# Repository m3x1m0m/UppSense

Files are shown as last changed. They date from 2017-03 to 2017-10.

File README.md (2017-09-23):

UppSense

UppSense17- Open Source sensor for chemical analysis based on fuoresence.
 
## Hardware
Hardware Block Diagram

The hardware consists out of three PCBs so far: An analog PCB, a digital PCB and an active Backplane. Two PCBs are developed with KiCAD. One is developed with Altium.

A transimpedance amplifier is used to convert light into a voltage. With a
second stage this voltage is amplified. Both outputs are available for the ADC. 

On the digital board there is besides an ESP8266, an ADC, a DAC and a temperature
sensor. The DAC is needed to steer the LED driver circuit, that excites the
sample. 
 
## Software
UML Diagram

The software is written in C++ leveraging the
[Sming](https://github.com/SmingHub/Sming) framework. This enables IoT
applications very easily.

In the UML diagram above it is examplarily shown how the software works. Providers
and receivers can be tied together in pairs to enable an easy way to exchange
data. 

[Software Documentation](http://uppsense.eu/swdoc/)

## Web & Contact
Website: www.uppsense.eu | Email: contact@uppsense.eu

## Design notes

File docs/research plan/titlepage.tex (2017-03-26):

%%%%%%%%%%%%%%%%%%%%%%%%%%%%%%%%%%%%%%%%%%%%%%%%%%%%%%%%%%%%%%%%%%%%%%%%%%%%%%%%%%%%%%
%% Author:      Maximilian Stiefel
%% Date:        06.03.2017
%% University:  Uppsala Universitet
%% Department:  Institutionen för informationsteknologi 
%% Course:      Microcontroller Programming
%% Project:     Swakeup
%%%%%%%%%%%%%%%%%%%%%%%%%%%%%%%%%%%%%%%%%%%%%%%%%%%%%%%%%%%%%%%%%%%%%%%%%%%%%%%%%%%%%%

\begin{titlepage}
% temporary margins only for titlepage
\newgeometry{lmargin={2cm},rmargin={2cm},tmargin={1cm},bmargin={2cm}}

%---------------------- Figures --------------------------------------------------

\begin{figure}
	\raggedright
	%\raggedleft
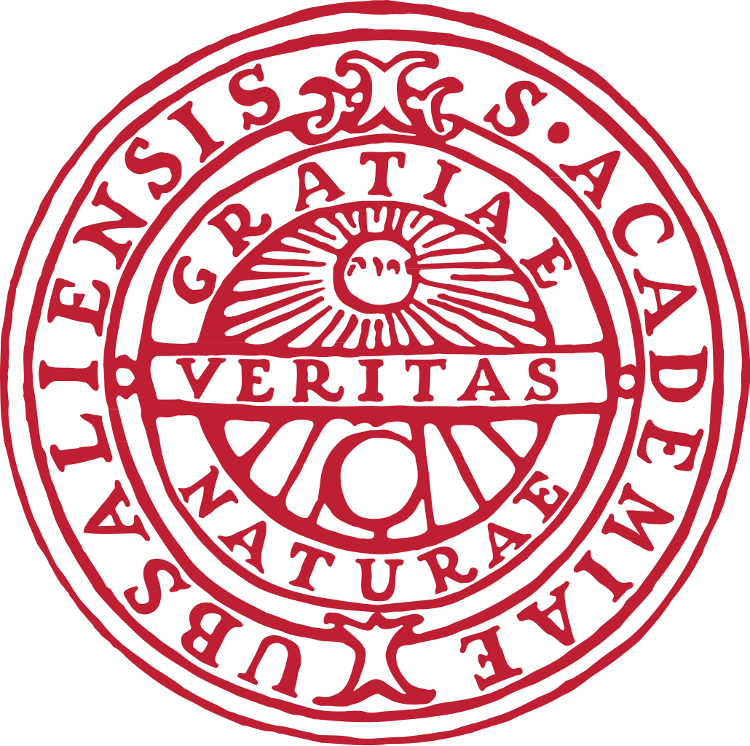
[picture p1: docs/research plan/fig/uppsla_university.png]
	
\end{figure}

%---------------------- Text -----------------------------------------------------

\begin{center}
	\vspace*{0pt}
	\begin{Huge}
		\textbf{\mytitle}\\
	\end{Huge}
	\vspace*{4em}
	\begin{LARGE}
		\textbf{\MakeUppercase{\mytypeofwork}}\\
	\end{LARGE}	
	\vspace*{2em}
	within the lecture of\\
	\mycourse\\
	\vspace*{2em}
	at \myuniversity\\
	in the Departement of \mydepartement\\
	\vspace*{2em}
	\myauthora{}, \myauthorb{} and \myauthorc\\
	\vspace*{2em}
	Deadline: \myduedate\\
	\vspace*{3em}
	\vfill
%---------------------- Table ----------------------------------------------------
	
	\setlength{\tabcolsep}{24pt}	% change space between rows
	\begin{tabular}{ll}
		Processing Period:&  \myperiod\\
		Supervisor:&\mytutor\\
		Document Revision:& \myrev\\
		Last Change:& \today\\
	\end{tabular}
	\setlength{\tabcolsep}{6pt}		% back to default
	\restoregeometry
\end{center}
\end{titlepage}
\clearpage

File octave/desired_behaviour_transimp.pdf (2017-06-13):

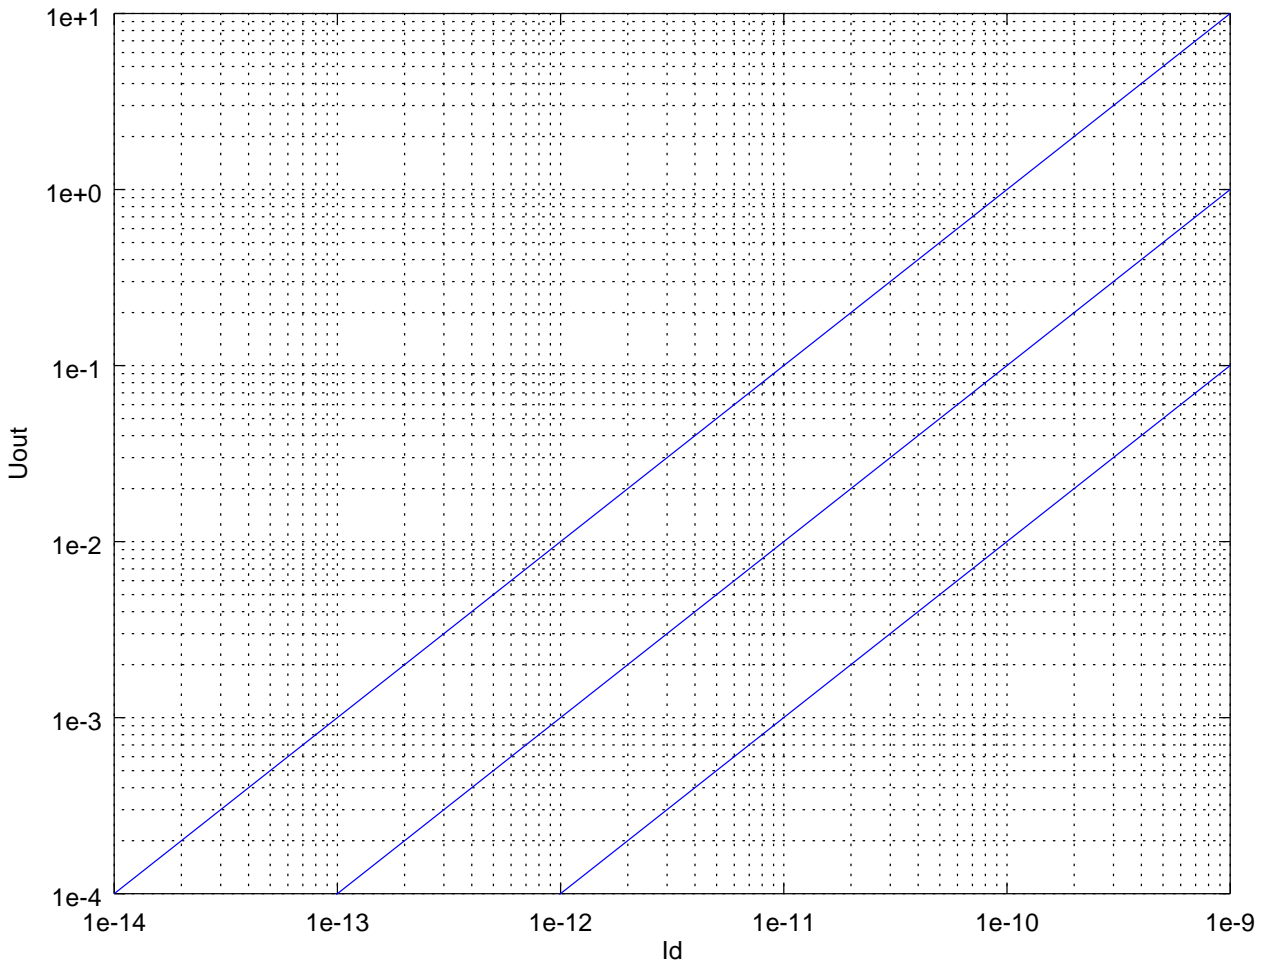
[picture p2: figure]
Uout

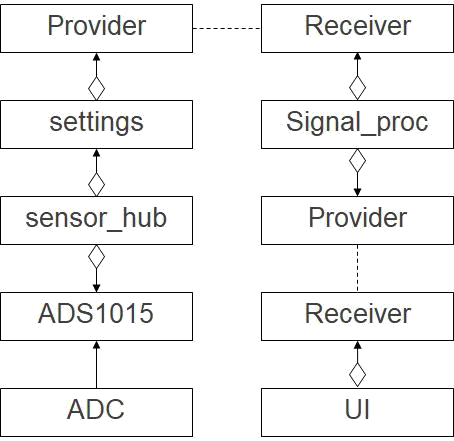
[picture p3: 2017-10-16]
docs/presentations/fig/sw_architecture.png

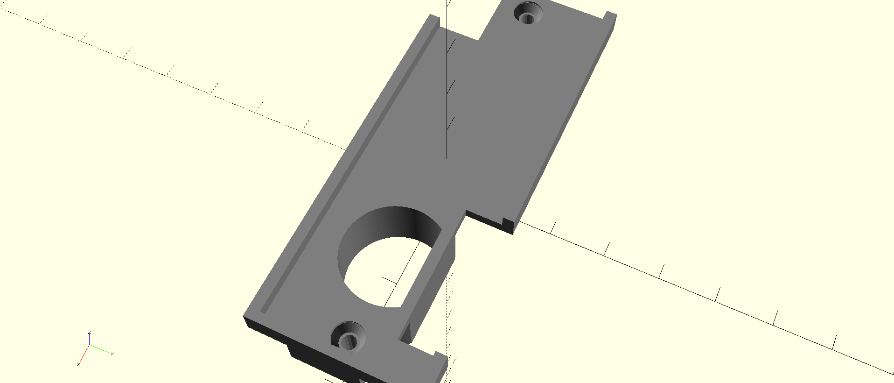
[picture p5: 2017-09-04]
cad/mechanics_rev6/pcb/screen_shot_2.png

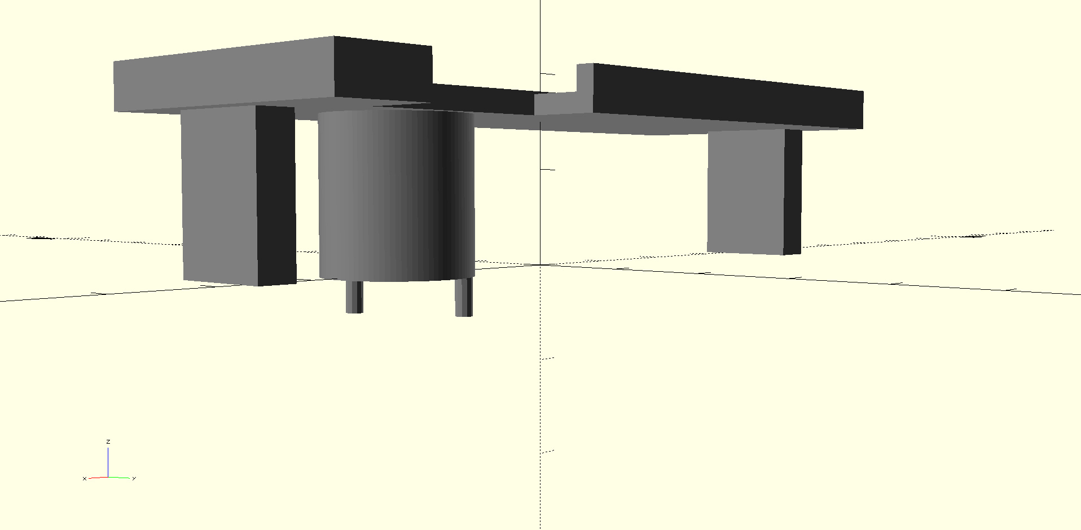
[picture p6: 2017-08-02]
cad/mechanics_rev6/pcb/screenshot_2.png

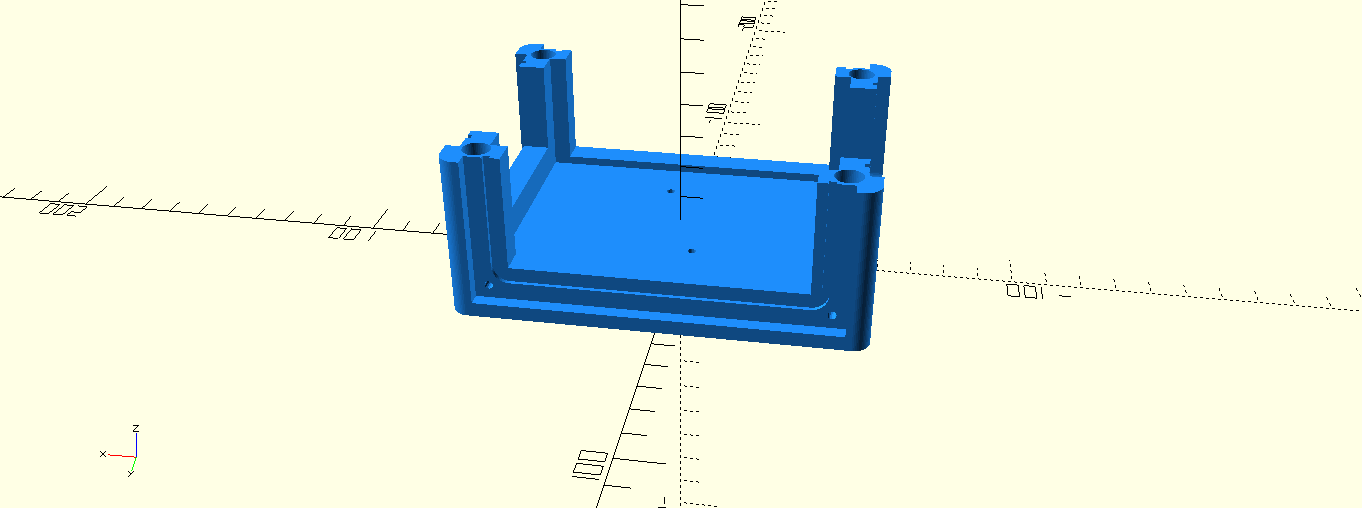
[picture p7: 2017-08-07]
cad/mechanics_rev6/housing/screenshot_female.png

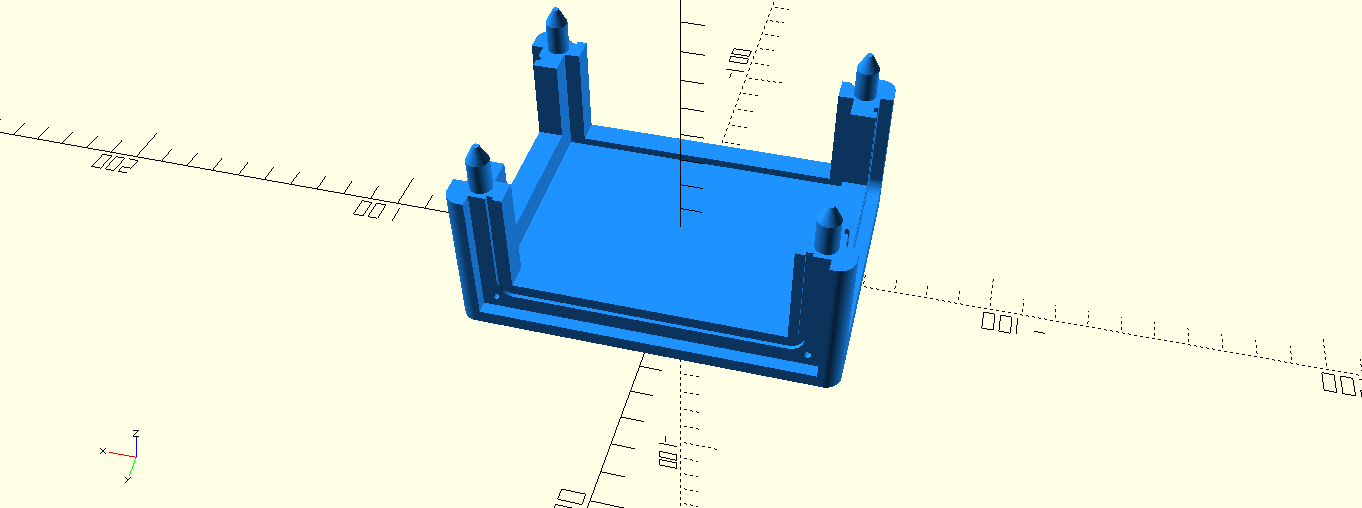
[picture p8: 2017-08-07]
cad/mechanics_rev6/housing/screenshot_male.png

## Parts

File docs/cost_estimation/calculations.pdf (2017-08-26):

Sheet1

Total | €40.00
Margin | €11.03
Ananlog Board | Price | Number
Passives | €0.05 | 34 €1.70
BPW34FA | €0.40 | 1 €0.40
BPW34 | €0.40 | 1 €0.40
UV LED | €0.10 | 1 €0.10
Connector Samtec 02x03 | €1.00 | 1 €1.00
Connector Samtec 02x07 | €1.00 | 1 €1.00
Transistor MMBT3904 | €0.05 | 1 €0.05
Opamp LTC6268 | €3.20 | 1 €3.20
Opamp ADA4522 | €1.20 | 1 €1.20
Opamp LM358 | €0.07 | 1 €0.07
Charge Pump ICL7660S | €0.09 | 2 €0.18
PCB | €0.50 | 1 €0.50
| | €9.80
Digital Board | Price | Number
Passives | €0.05 | 26 €1.30
ADS1115 | €3.00 | 1 €3.00
DAC101C085 | €0.70 | 1 €0.70
MCP9808 | €0.70 | 1 €0.70
Connector Samtec Male 02x03 | €1.00 | 1 €1.00
Connector Samtec male 02x07 | €1.00 | 1 €1.00
ESP8266 | €1.50 | 1 €1.50
PCB | €0.50 | 1 €0.50
| | €9.70
Backplane | Price | Number
Passives | €0.05 | 23 €1.15
Signaling LEDs | €0.09 | 6 €0.09
USB Connector | €0.40 | 1 €0.40
Transistor MMBT3904 | €0.05 | 1 €0.05
P MOSFET | €0.30 | 1 €0.30
Opamp LM358 | €0.07 | 2 €0.14
LDO Voltage Regulator | €0.30 | 1 €0.30
CH340G USB2UART | €0.30 | 1 €0.30
Crystal 12 MHz | €0.10 | 1 €0.10
Connector Samtec Female 02x03 | €1.50 | 1 €1.50
Connector Samtec Female 02x07 | €1.50 | 1 €1.50
PCB | €0.50 | 1 €0.50
| | €6.33
Mechanics | Price | Number
Screws | €0.06 | 22 €1.32
Helicoil for threads | €0.06 | 22 €1.32
O-rings | €0.50 | 1 €0.50
3D Parts | €5.00 | 1 €5.00
| | €3.14

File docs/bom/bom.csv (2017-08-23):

Component | Farnell Order Code | Quantity
C 0805 10u | 1833812 | 15
C 0603 4.7uF | 2496930 | 10
C 0805 1u | 2496946 | 30
C 0805 0.1u | 499687 | 40
C 0805 10n | 1414662 | 40
R 0805 1M | 1576507 | 20
R 0805 33k | 2078965 | 10
R 0603 10k | 2447230 | 10
R 0603 2.4k | 2059611 | 10
R 0805 2.4k | 2502703 | 20
R 0603 1k | 9238484 | 10
R 0805 1k | 9237496 | 30
R 0603 470R | 9332146 | 10
R 0805 470R | 2447662 | 30
R0805 100R | 9237364 | 20
R 0603 0R | 2447743 | 100
3.3V LDO TC1262 | 1296594 | 3
Crystal 12 Mhz | 9713344 | 5
Opamp ADA4522 | 2505560 | 5
Charge Pump ICL7660 | 1561969 | 5
Opamp AD8616 | 1581952 | 2
2 NiMH AAA Batteries | 1662656 | 2
Micro USB Type B | 2554980 | 3
Si2323 | 1470106 | 3
Opamp LTC6268 | 2464182 | 2
ADC | 1778211 | 3
Temp sensor ic | 2080523 | 3
Opamp LM358 | 1564331 | 10
LEDs | 1581242 | 15
New filter | 177143 | 1
Screws M3 | 2494521 | 50

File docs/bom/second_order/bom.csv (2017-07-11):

Component | Farnell Order Code | Quantity
C 0805 10u | 1833812 | 15
C 0603 4.7uF | 2496930 | 10
C 0805 1u | 2496946 | 30
C 0603 100nF | 2496825 | 10
C 0805 0.1u | 499687 | 40
C 0805 10n | 1414662 | 40
C 0805 22pf | 1759489 | 20
R 0805 10G | 2420567 | 2
R 0805 100M | 9236511 | 10
R 0805 1M | 1576507 | 10
R 0805 100k | 2447551 | 100
R 0603 10k | 2447230 | 10
R 0805 10k | 9237755 | 30
R 0603 2.4k | 2059611 | 10
R 0805 2.4k | 2502703 | 20
R 0603 1k | 9238484 | 10
R 0805 1k | 9237496 | 30
R 0603 470R | 9332146 | 10
R 0805 470R | 2447662 | 30
3.3V LDO TC1262 | 1296594 | 3
Crystal 12 Mhz | 9713344 | 5
PMOS | 2061419 | 5
NMOS | 1864589 | 5
Poti | 2550676 | 3
Opamp ADA4522 | 2505560 | 2
Charge Pump ICL7660 | 1561969 | 3
Opamp AD8616 | 1581952 | 2
2 NiMH AAA Batteries | 1662656 | 2
Battery Holder AAA | 1650687 | 2
Micro USB Type B | 2554980 | 3
MMBT3904 | 2535650 | 20
Si2323 | 1470106 | 3
Opamp LTC6268 | 2464182 | 2
ADC | 1778211 | 3
Temp sensor ic | 2080523 | 3
Opamp LM358 | 1564331 | 10
LEDs | 1581242 | 15

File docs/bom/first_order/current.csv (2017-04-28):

Article | Farnell Ordercode | Quantity
Resistior 100 Ohm | 2504961 | 10
MMBT3904 | 1773602 | 20
Resistor 1k | 9237496 | 20
Resistor 5.1 ohm | 2502734 | 50
Resistor 19.1k | 2303683 | 50
Header right angle | 9731199 | 10

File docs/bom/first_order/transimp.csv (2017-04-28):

Article | Farnell Ordercode | Quantity
Opamp | AD8616ARZ | 5
Jumper | 2396303 | 15
R 10k | 9237755 | 100
R 100k | 2447551 | 100
R 1M | 1576507 | 10
R 10M | 9238115 | 100
R 100M | 9236511 | 10
C 10n | 1414662 | 100
C 1n | 2496935 | 100
C 100p | 2332782 | 10
C 10p | 1759191 | 100
C 1p | 1759179 | 50
M3 screw 8 mm | 2494521 | 50
M3 spacing bolts female-male 8 mm | 1466795 | 8
M3 spacing bolts female-female 30 mm | 1466803 | 8
Washer M3 | 1377496 | 1
Raw PCB single-sided euro | 1267751 | 2
Raw PCB double-sided euro | 149058 | 2
MOSFET | 1831089 | 10

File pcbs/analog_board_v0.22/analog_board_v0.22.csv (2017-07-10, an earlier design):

Title | SensUs Sensor Board
Revision | v.0.2
Date | 2017-07-05
Generated | mån 10 jul 2017 09:42:13
Company | UppSense Heart Failure Diagnostics
Comment 1
Comment 2
Comment 3
Comment 4
Total Parts | 71
Total Unique Parts | 33
Ref | Qty | Value | Footprint | Farnell | Samtec
C1 C4 C14 C15 C20 | 5 | 1u | Resistors_SMD:R_0805 | 2496946
C2 C5 C8 C11 C12 C13 C16 C21 C23 | 9 | 100n | Resistors_SMD:R_0805 | 499687
C3 C6 C9 C10 C22 | 5 | 10n | Resistors_SMD:R_0805 | 1414662
C7 | 1 | 26f | Embedded Caps:EMBEDDED_CAP_1mm
C17 C18 | 2 | 10u | Resistors_SMD:R_0805 | 1833812
C19 | 1 | 1u | Resistors_SMD:R_0805 | 1845751
D1 | 1 | BPW34 | Photodiodes:BPW34FA_w_Silks | 1045425
D2 | 1 | LED | LEDs:LED_D5.0mm
D3 | 1 | BPW34 | Photodiodes:BPW34FA | 1045425
IC1 IC1 IC2 IC3 IC4 IC21 IC22 IC33 | 8 | TEST | Tespoints:TP_SMD_quadr_1mm
J1 | 1 | CONN_02X03 | Pin_Headers:Pin_Header_Angled_2x03_Pitch2.54mm |  | TSW-103-08-G-D-RA
J2 | 1 | CONN_02X07 | Pin_Headers:Pin_Header_Angled_2x07_Pitch2.54mm |  | TSW-107-08-G-D-RA
J3 | 1 | CONN_01X04 | China Connectors:LED_CONN_1.25_PITCH
J4 | 1 | CONN_01X01 | Guard Connector:GuardConnector
P1 P2 P3 | 3 | CONN_01X03 | Samtec Connectors:Samtec-PHT-1-3-01-L-S
Q1 Q3 Q5 Q7 | 4 | DMP2035U | TO_SOT_Packages_SMD:SOT-23 | 2061419
Q2 Q4 Q6 Q8 | 4 | TSM2314 | TO_SOT_Packages_SMD:SOT-23 | 1864589
Q9 | 1 | MMBT3904 | TO_SOT_Packages_SMD:SOT-23 | 1757935
R1 | 1 | 100M | WithoutSilkscreen:R_0805_W_Silks | 9236511
R2 R5 R6 | 3 | 2.4k | Resistors_SMD:R_0805 | 2502703
R3 R8 | 2 | 1k | Resistors_SMD:R_0805 | 9237496
R4 R10 R12 | 3 | 100k | Resistors_SMD:R_0805 | 2447551
R7 R13 | 2 | 1M | Resistors_SMD:R_0805 | 1576507
R9 | 1 | 100R | Resistors_SMD:R_0805 | 1632456
R11 | 1 | 10k | Resistors_SMD:R_0805 | 9237755
R14 | 1 | 1k | WithoutSilkscreen:R_0805_W_Silks | 9237496
R15 | 1 | 100k | WithoutSilkscreen:R_0805_W_Silks | 2447551
RV1 | 1 | T73YE103KT20 | MyPotis:Vishay_T73YE103KT20 | 2550676
TP1 | 1 | DAC2 | Tespoints:TP_SMD_quadr_1mm
U1 | 1 | LTC6268IS8#PBF | WithoutSilkscreen:SOIC-8-N-W-Silks | 2464182
U2 | 1 | ADA4522-2ARZ | SMD_Packages:SOIC-8-N | 2505560
U3 | 1 | ICL7660S | SMD_Packages:SOIC-8-N | 1561969
U4 | 1 | AD8616 | SMD_Packages:SOIC-8-N | 1581952
BOM made with KICAD_BOM_WIZARD (https://github.com/HashDefineElectronics/KiCad_BOM_Wizard.git)
Generated mån 10 jul 2017 09:42:13

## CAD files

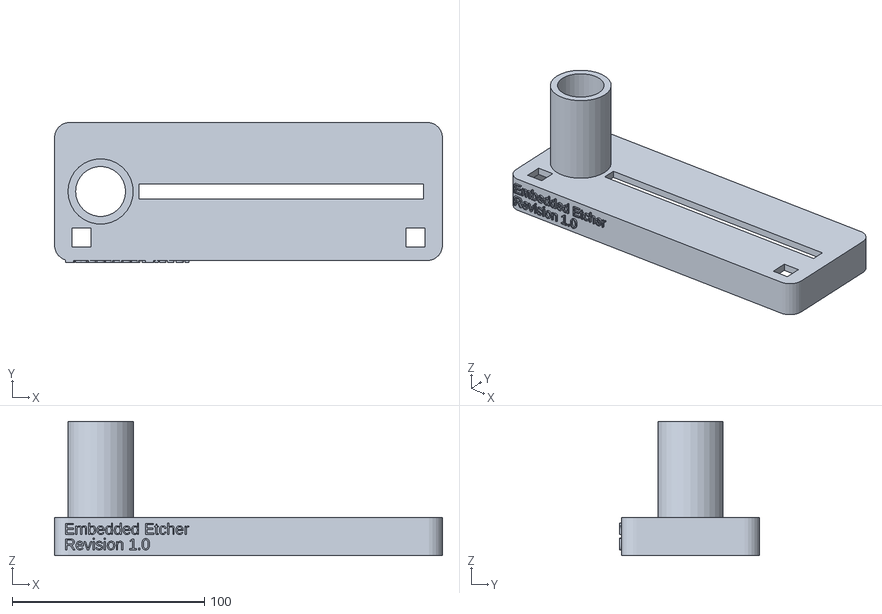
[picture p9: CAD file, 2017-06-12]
cad/etching_machine/v2.0/pcb_holder_lid.stl
202.0 x 72.9 x 70.0

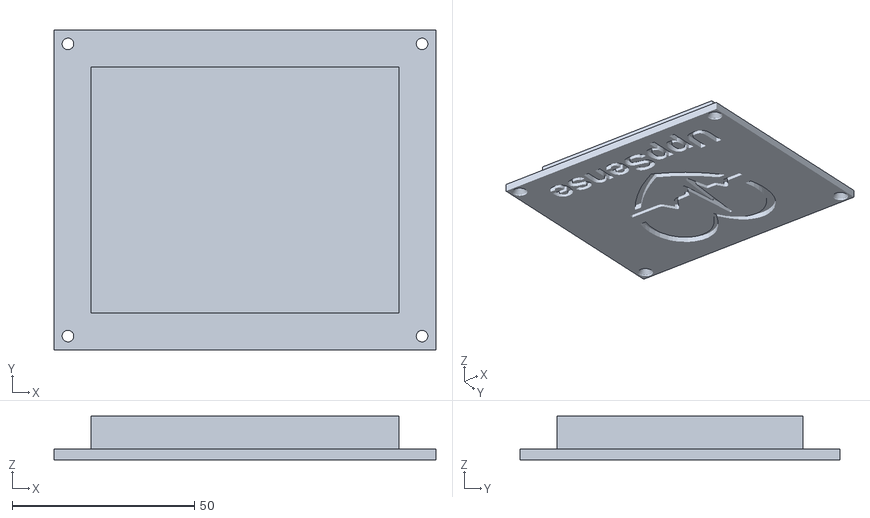
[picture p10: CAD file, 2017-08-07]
cad/mechanics_rev6/housing/lid_front.stl
104.9 x 87.9 x 12.0

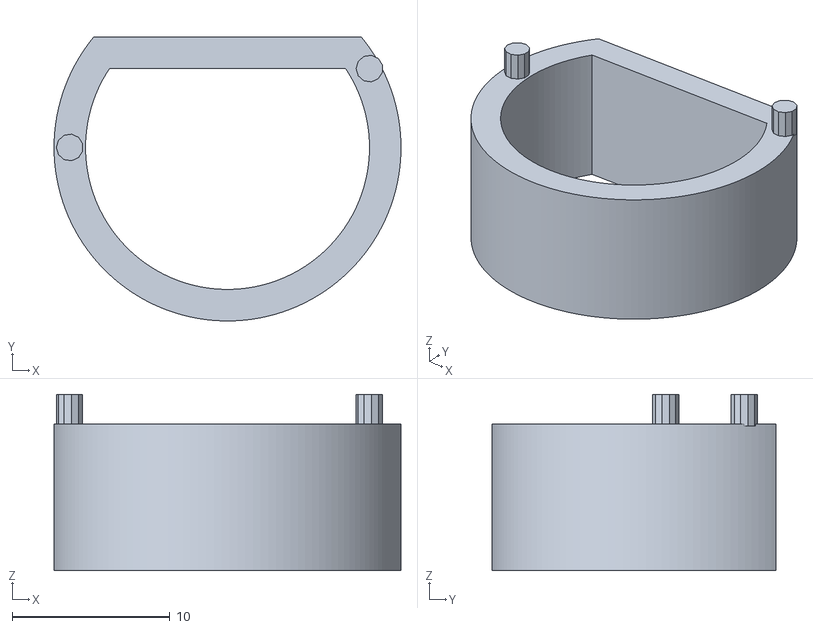
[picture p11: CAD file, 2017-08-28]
cad/mechanics_rev6/pcb/illuminator.stl
22.0 x 18.0 x 11.2

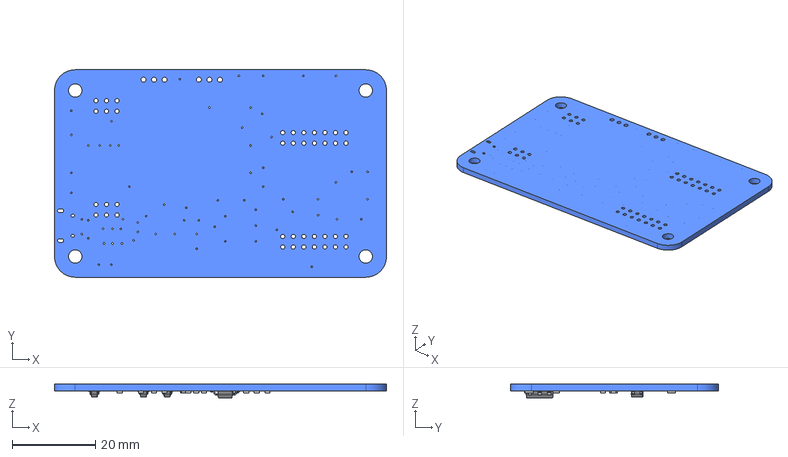
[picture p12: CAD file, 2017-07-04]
pcbs/backplane/backplane.step
80.0 x 50.0 x 3.30 mm
Pcb
R_0805_
R_0805_001
R_0805_002
R_0805_003
R_0805_004
R_0805_005
R_0805_006
R_0805_007
R_0805_008
SOT_23_
SOT_23_001
R_0805_009
R_0805_010
R_0805_011
R_0805_012
R_0805_013
R_0805_014
R_0805_015
R_0805_016
SOT_223_
SOT_23_002

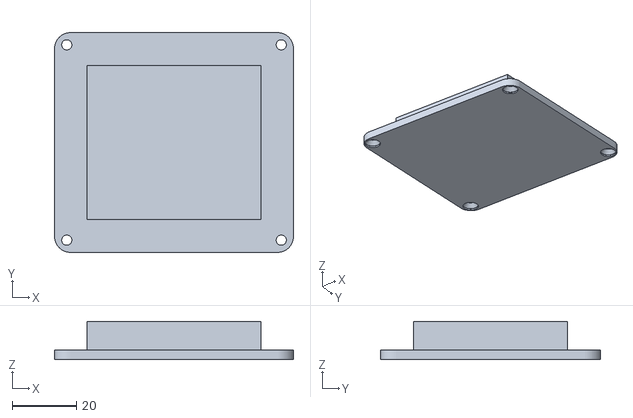
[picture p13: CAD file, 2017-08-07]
cad/mechanics_rev6/housing/lid_l_r.stl
74.6 x 68.6 x 12.0

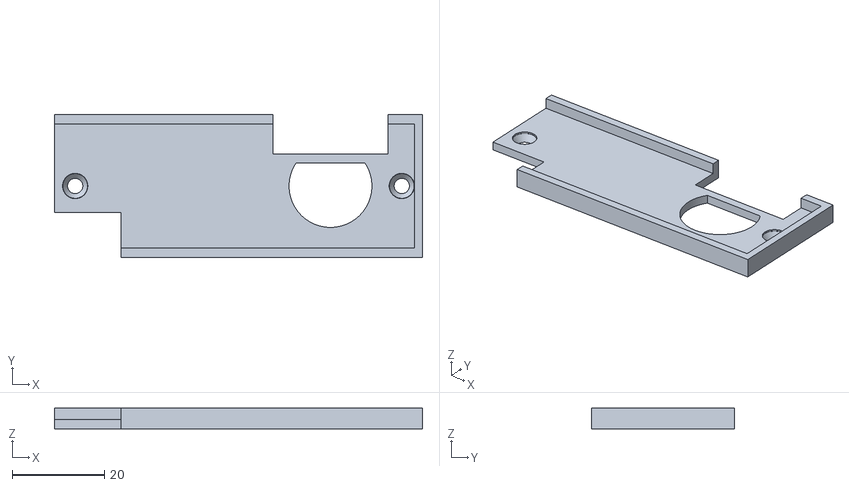
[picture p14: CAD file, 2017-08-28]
cad/mechanics_rev6/pcb/glass_holder.stl
80.0 x 31.0 x 4.50

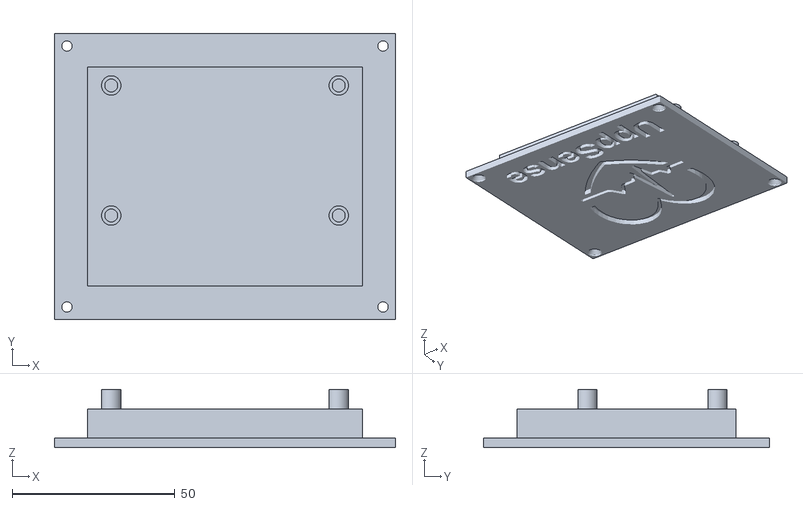
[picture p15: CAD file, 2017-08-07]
cad/mechanics_rev6/housing/lid_rear.stl
104.9 x 87.9 x 18.0

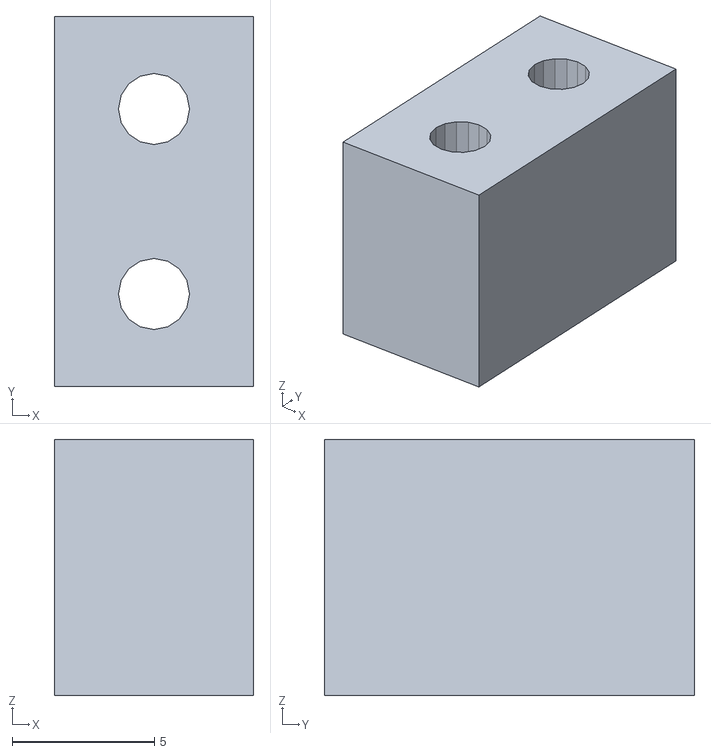
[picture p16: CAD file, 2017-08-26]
cad/mechanics_rev6/pcb/leg.stl
7.00 x 13.0 x 9.00

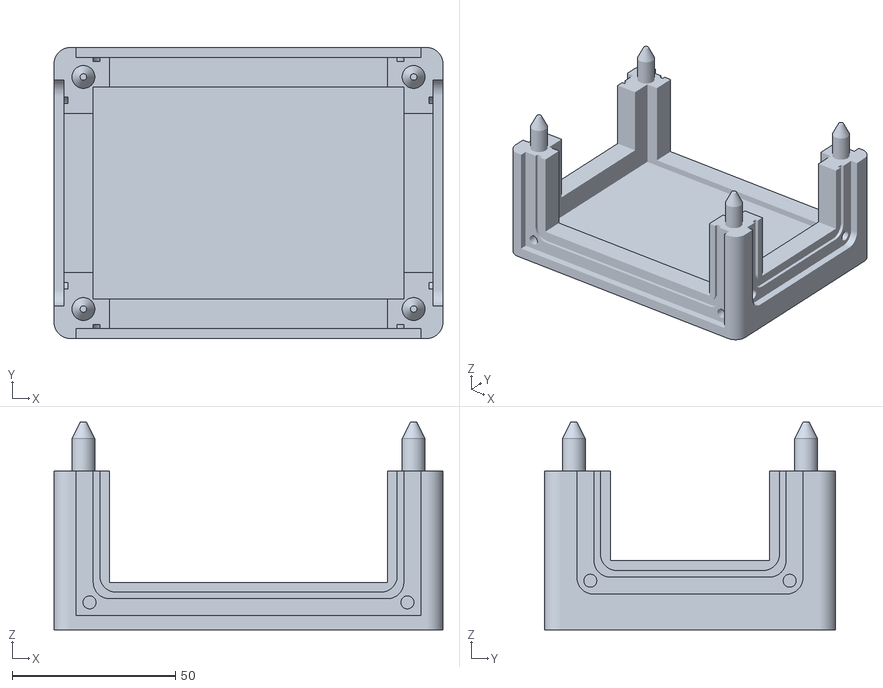
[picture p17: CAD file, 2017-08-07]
cad/mechanics_rev6/housing/box_male.stl
119.0 x 89.0 x 63.5

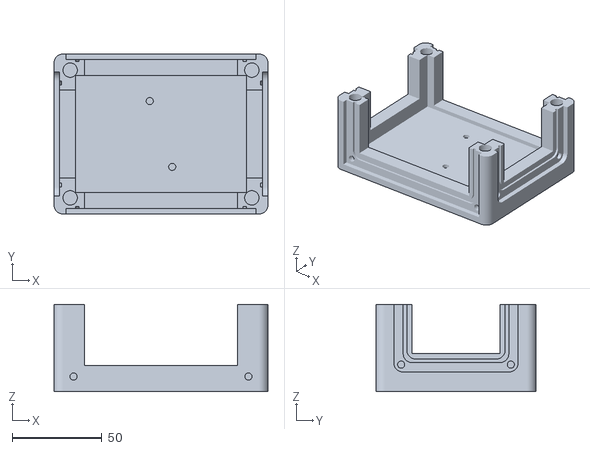
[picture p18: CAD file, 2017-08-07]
cad/mechanics_rev6/housing/box_female.stl
119.0 x 89.0 x 48.5

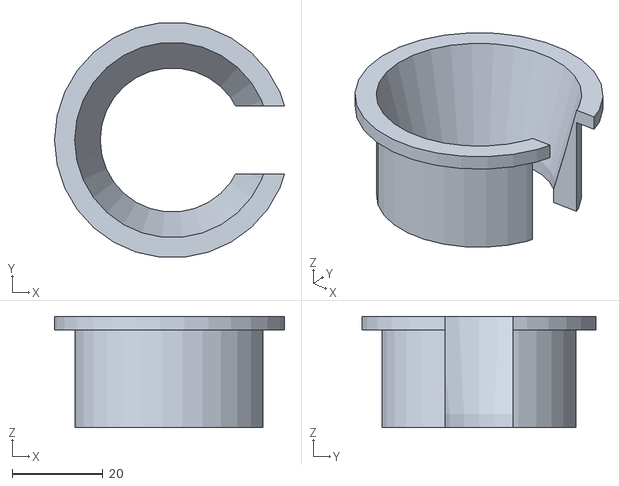
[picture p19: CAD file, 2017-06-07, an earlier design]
cad/mechanics_rev1/adapter_drilling_machine.stl
50.8 x 51.7 x 24.5

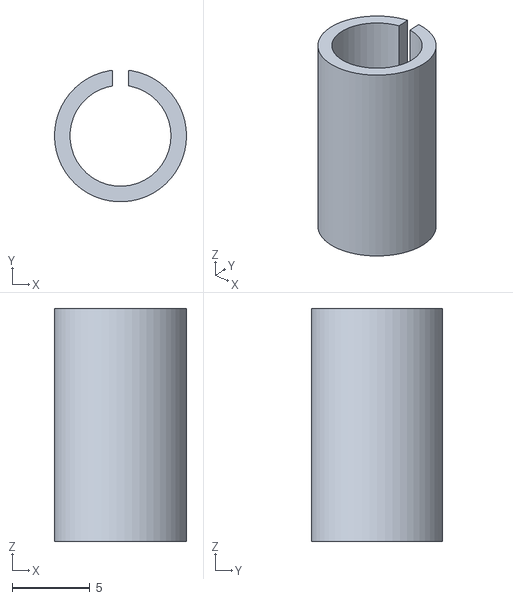
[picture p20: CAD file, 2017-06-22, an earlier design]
cad/mechanics_rev2/led_illuminator.stl
8.50 x 8.46 x 15.0

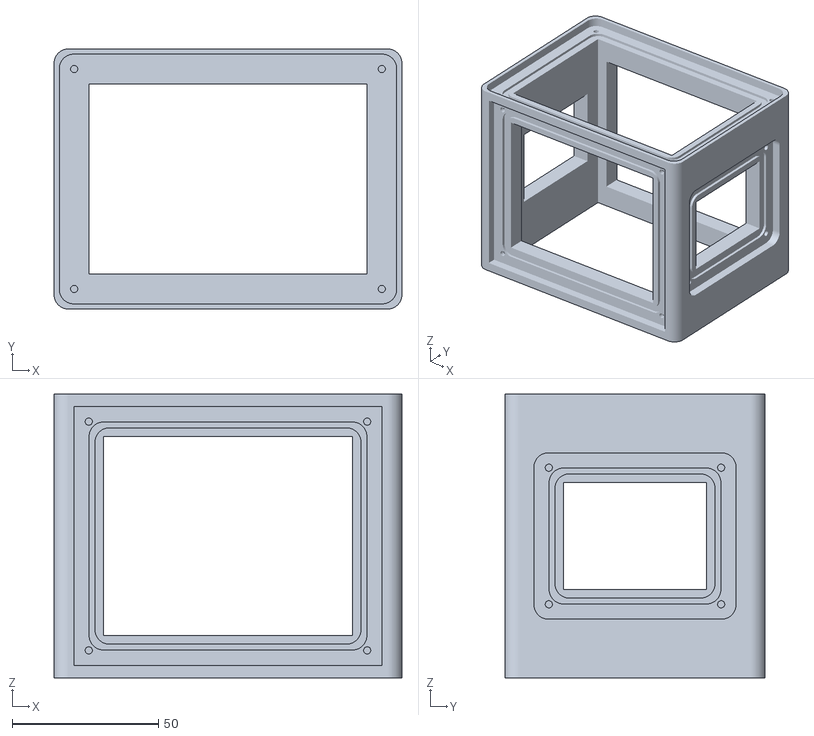
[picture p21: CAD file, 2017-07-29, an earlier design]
cad/mechanics_rev3/housing/box.stl
119.0 x 89.0 x 97.0

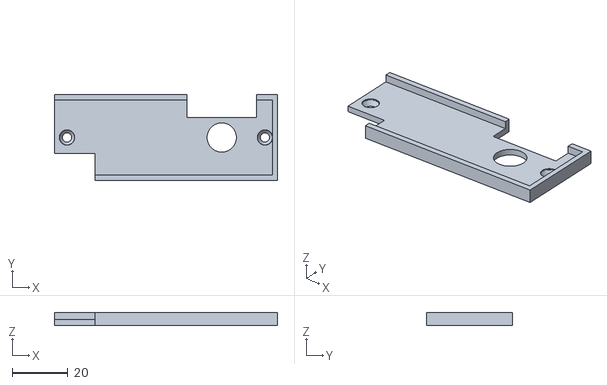
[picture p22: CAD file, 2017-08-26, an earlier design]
cad/mechanics_rev5/pcb/glass_holder.stl
80.0 x 31.0 x 4.50

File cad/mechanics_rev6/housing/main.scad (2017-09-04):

/////////////////////////////////////////////////////////////////////////////////
// Main file to assemble everything.
//
// Author:              Maximilian Stiefel
// Last modification:   20.07.2017
/////////////////////////////////////////////////////////////////////////////////

/////////////////////////////////////////////////////////////////////////////////
// Includes
/////////////////////////////////////////////////////////////////////////////////

// Dimesnions
include <dimensions.scad>
use <dimensions.scad>

// Module for male part of raw box
include <box_male.scad>
use <box_male.scad>

// Module for female part of raw box
include <box_female.scad>
use <box_female.scad>

// Module for raw box without any lids
include <lid_l_r.scad>
use <lid_l_r.scad>

// Module for raw box without any lids
include <lid_f_b.scad>
use <lid_f_b.scad>

// Module for raw box without any lids
include <lid_t_b.scad>
use <lid_t_b.scad>

////////////////////////////////////////////////////////////////////////////////
// Vars
/////////////////////////////////////////////////////////////////////////////////
// 0 = put lids, 1 = remove lids
close = 1;
// Set minimum angle of a fragment
$fa = 0.5;
// Set minimum size of a fragment
$fs = 0.5;

////////////////////////////////////////////////////////////////////////////////
// Action
/////////////////////////////////////////////////////////////////////////////////
//difference()
//{
union()
{
color(myColor1)
{
// Lid right
translate([housing_outside_width/2 + close*20, 0, 0])
rotate([0, 0, 0])
lid_l_r();

// Lid left
translate([-housing_outside_width/2 - close*20, 0, 0])
rotate([0, 180, 0])
lid_l_r();

// Lid front
translate([0, -housing_outside_depth/2 - close*20, 0])
rotate([90, 0, 0])
//rotate([0, 180, 0])
lid_f_b(1,0);

// Lid back
translate([0, +housing_outside_depth/2 + close*20, 0])
rotate([-90, 180, 0])
//rotate([0, 180, 0])
lid_f_b(1,1);

color(myColor1, 0.8)
translate([0, 0, close*10 +0.0])
//translate([0, 0, housing_outside_height/2])
//rotate([0,180,0])
box_male();
translate([0, 0, -close*10 -0.0])
//translate([0, 0, housing_outside_height/2])
box_female();
}
}
//translate([-200, 0, 0])
//cube([400,400,400], center=true);
//}

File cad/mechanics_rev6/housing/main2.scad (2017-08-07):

/////////////////////////////////////////////////////////////////////////////////
// Main file to assemble everything.
//
// Author:              Maximilian Stiefel
// Last modification:   20.07.2017
/////////////////////////////////////////////////////////////////////////////////

/////////////////////////////////////////////////////////////////////////////////
// Includes
/////////////////////////////////////////////////////////////////////////////////

// Dimesnions
include <dimensions.scad>
use <dimensions.scad>

// Module for raw box without any lids
include <box.scad>
use <box.scad>

// Module for raw box without any lids
include <lid_l_r.scad>
use <lid_l_r.scad>

// Module for raw box without any lids
include <lid_f_b.scad>
use <lid_f_b.scad>

// Module for raw box without any lids
include <lid_t_b.scad>
use <lid_t_b.scad>

////////////////////////////////////////////////////////////////////////////////
// Vars
/////////////////////////////////////////////////////////////////////////////////
// 0 = put lids, 1 = remove lids
close = 0;
// Set minimum angle of a fragment
$fa = 0.5;
// Set minimum size of a fragment
$fs = 0.5;

////////////////////////////////////////////////////////////////////////////////
// Action
/////////////////////////////////////////////////////////////////////////////////
//difference()
//{
union()
{
color(myColor1)
{
// Lid right
translate([housing_outside_width/2 + close*20, 0, 0])
rotate([0, 0, 0])
lid_l_r();

// Lid left
translate([-housing_outside_width/2 - close*20, 0, 0])
rotate([0, 180, 0])
lid_l_r();

// Lid front
translate([0, -housing_outside_depth/2 - close*20, 0])
rotate([90, 0, 0])
lid_f_b(1,0);

// Lid back
translate([0, +housing_outside_depth/2 + close*20, 0])
rotate([-90, 180, 0])
lid_f_b(1,1);

color(myColor1, 0.8)
box();
}
}
//translate([-200, 0, 0])
//cube([400,400,400], center=true);
//}

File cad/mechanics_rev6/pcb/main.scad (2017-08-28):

/////////////////////////////////////////////////////////////////////////////////
// Main file to bring everything together. 
//
// Author:              Maximilian Stiefel
// Last modification:   29.06.2017
/////////////////////////////////////////////////////////////////////////////////

/////////////////////////////////////////////////////////////////////////////////
// Includes
/////////////////////////////////////////////////////////////////////////////////

// Dimesnions
include <dimensions.scad>
use <dimensions.scad>

// Module for the glass holder
include <glass_holder.scad>
use <glass_holder.scad>

// Module for the legs 
include <legs.scad>
use <legs.scad>

// Module for the legs 
include <led_illuminator.scad>
use <led_illuminator.scad>

/////////////////////////////////////////////////////////////////////////////////
// Vars
/////////////////////////////////////////////////////////////////////////////////
$fa = 0.5; // minimum facet angle is now 0.5
$fs = 0.5; // minimum facet size is now 0.5 mm

/////////////////////////////////////////////////////////////////////////////////
// Action
/////////////////////////////////////////////////////////////////////////////////
color(myColor1)
{
	// Glass holder
	translate([0, 0, holder_height/2 + leg_height -0.01])
	//translate([0, 0, holder_height/2])	
	glass_holder();
	
	// Legs
	translate([glass_slide_width/2 - leg_pos_x, 0, 0])
	legs();
	
	translate([-glass_slide_width/2 + leg_pos_x, 0, 0])
	rotate([0, 0, 180])
	legs();
	
	translate([glass_slide_width/2 - led_pos_x, 0, led_illuminator_height/2 + 0.01])	
//	translate([0, 0, (led_illuminator_height + allowance03)/2])
//	rotate([0, 180 ,0])
	illuminator();
}

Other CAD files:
cad/mechanics_rev6/housing/logo_taylored.dxf
cad/mechanics_rev6/housing/logo.dxf
cad/mechanics_rev1/housing.step
cad/mechanics_rev2/spacers.stl
cad/mechanics_rev6/housing/box.scad
cad/mechanics_rev1/adapter.scad
cad/mechanics_rev1/adapter.step
cad/mechanics_rev1/adapter.stl
cad/mechanics_rev1/adapter_drilling_machine.scad
cad/mechanics_rev1/housing.scad
cad/mechanics_rev1/housing.stl
cad/mechanics_rev1/lid.scad
cad/mechanics_rev1/lid.step
cad/mechanics_rev1/lid.stl
cad/mechanics_rev2/glass_slide_holder.stl
cad/mechanics_rev2/spacers.scad
cad/mechanics_rev3/housing/lid_bottom.stl
cad/mechanics_rev3/pcb/glass_slide_holder.scad
cad/mechanics_rev5/pcb/dimensions.scad
cad/mechanics_rev5/pcb/glass_holder.scad
cad/mechanics_rev5/pcb/illuminator.stl
cad/mechanics_rev5/pcb/led_illuminator.scad
cad/mechanics_rev5/pcb/main.scad
cad/mechanics_rev6/housing/box_female.scad
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

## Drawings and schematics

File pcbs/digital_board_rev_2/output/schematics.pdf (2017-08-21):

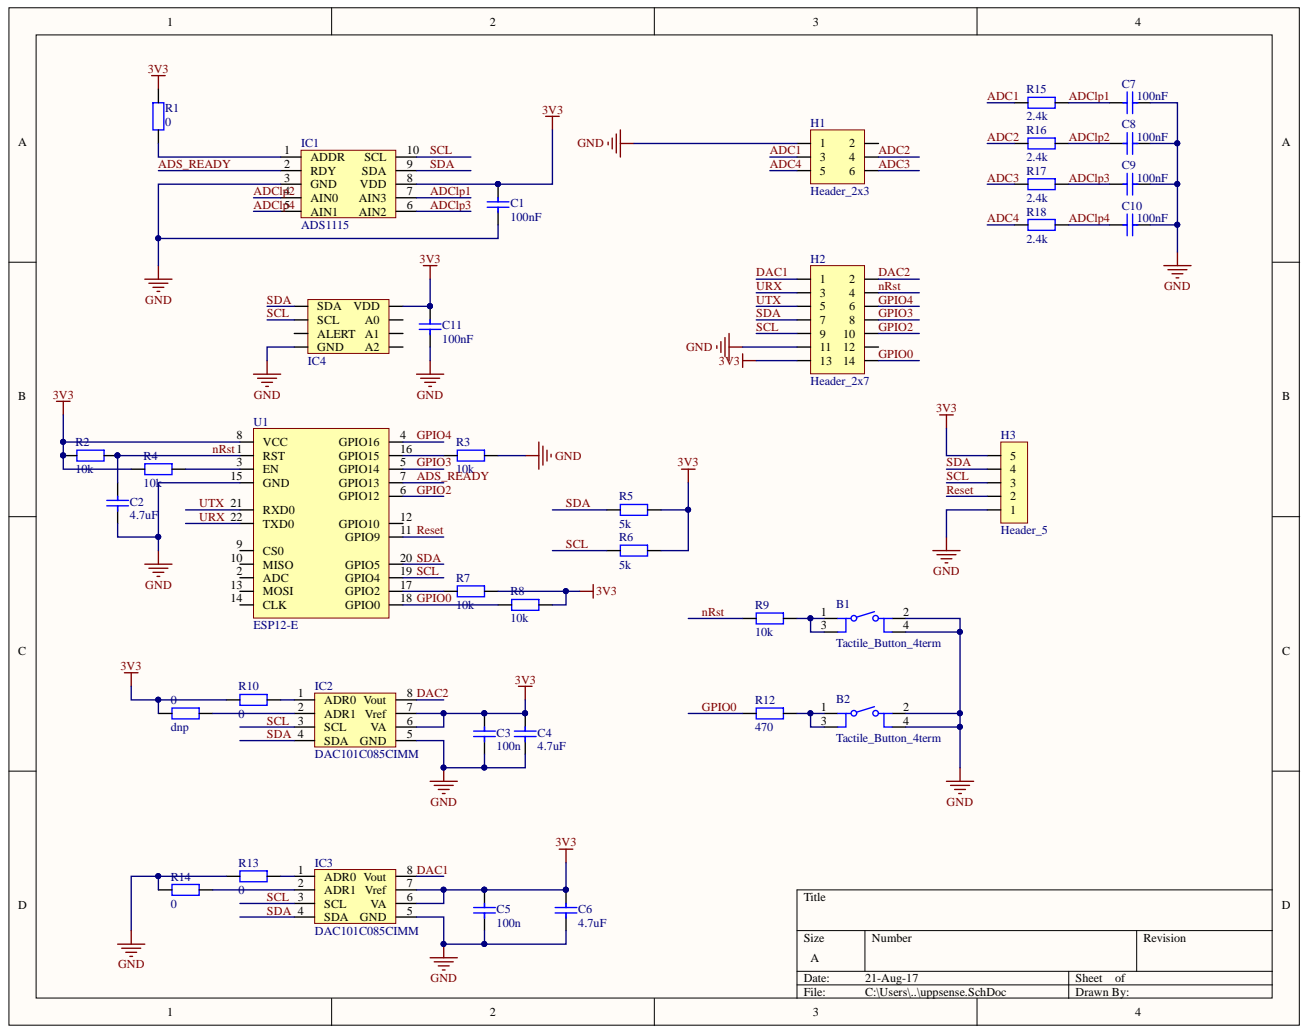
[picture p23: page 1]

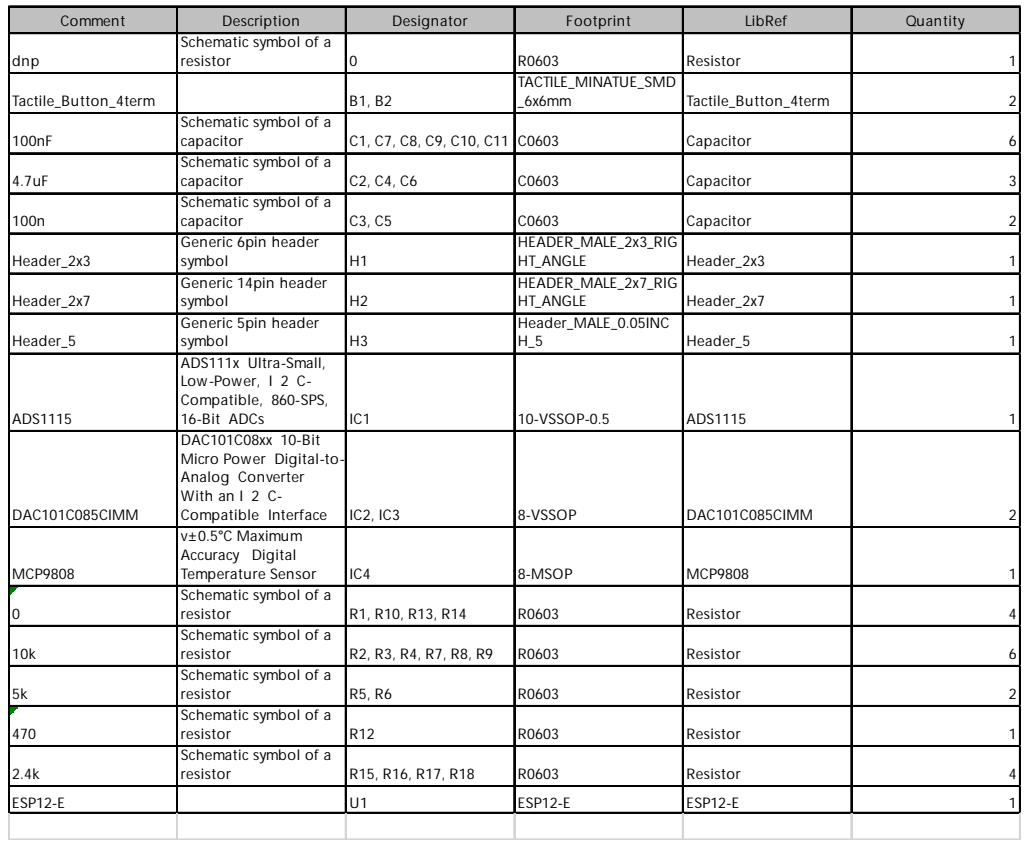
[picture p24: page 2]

Comment | Description | Designator | Footprint | LibRef | Quantity

dnp | Schematic symbol of a resistor | 0 | R0603 | Resistor | 1

Tactile_Button_4term | | B1, B2 | TACTILE_MINATUE_SMD _6x6mm | Tactile_Button_4term | 2

100nF | Schematic symbol of a capacitor | C1, C7, C8, C9, C10, C11 | C0603 | Capacitor | 6

4.7uF | Schematic symbol of a capacitor | C2, C4, C6 | C0603 | Capacitor | 3

100n | Schematic symbol of a capacitor | C3, C5 | C0603 | Capacitor | 2

Header_2x3 | Generic 6pin header symbol | H1 | HEADER_MALE_2x3_RIG HT_ANGLE | Header_2x3 | 1

Header_2x7 | Generic 14pin header symbol | H2 | HEADER_MALE_2x7_RIG HT_ANGLE | Header_2x7 | 1

Header_5 | Generic 5pin header symbol | H3 | Header_MALE_0.05INC H_5 | Header_5 | 1

ADS1115 | ADS111x Ultra-Small, Low-Power, I 2 C-Compatible, 860-SPS, 16-Bit ADCs | IC1 | 10-VSSOP-0.5 | ADS1115 | 1

DAC101C085CIMM | DAC101C08xx 10-Bit Micro Power Digital-to-Analog Converter With an I 2 C-Compatible Interface | IC2, IC3 | 8-VSSOP | DAC101C085CIMM | 2

MCP9808 | v±0.5°C Maximum Accuracy Digital Temperature Sensor | IC4 | 8-MSOP | MCP9808 | 1

0 | Schematic symbol of a resistor | R1, R10, R13, R14 | R0603 | Resistor | 4

10k | Schematic symbol of a resistor | R2, R3, R4, R7, R8, R9 | R0603 | Resistor | 6

5k | Schematic symbol of a resistor | R5, R6 | R0603 | Resistor | 2

470 | Schematic symbol of a resistor | R12 | R0603 | Resistor | 1

2.4k | Schematic symbol of a resistor | R15, R16, R17, R18 | R0603 | Resistor | 4

ESP12-E | | U1 | ESP12-E | ESP12-E | 1

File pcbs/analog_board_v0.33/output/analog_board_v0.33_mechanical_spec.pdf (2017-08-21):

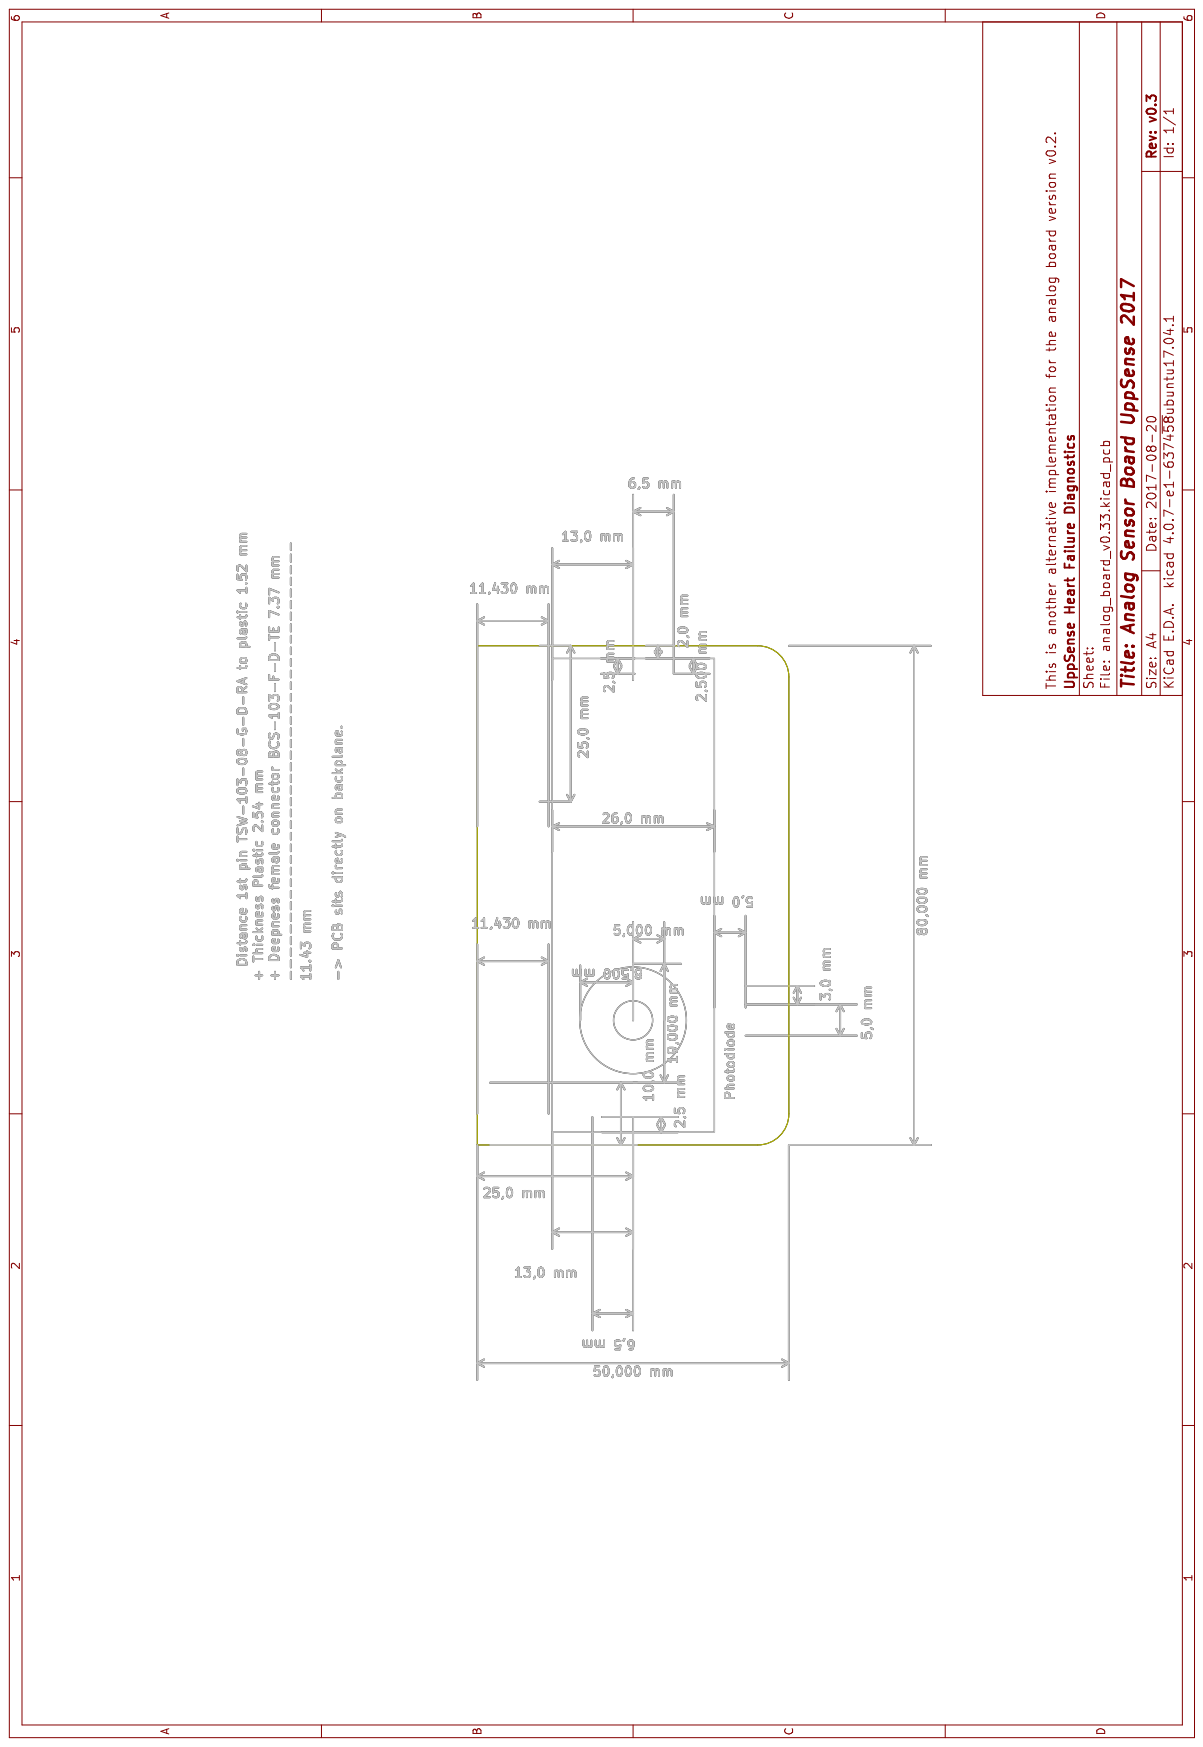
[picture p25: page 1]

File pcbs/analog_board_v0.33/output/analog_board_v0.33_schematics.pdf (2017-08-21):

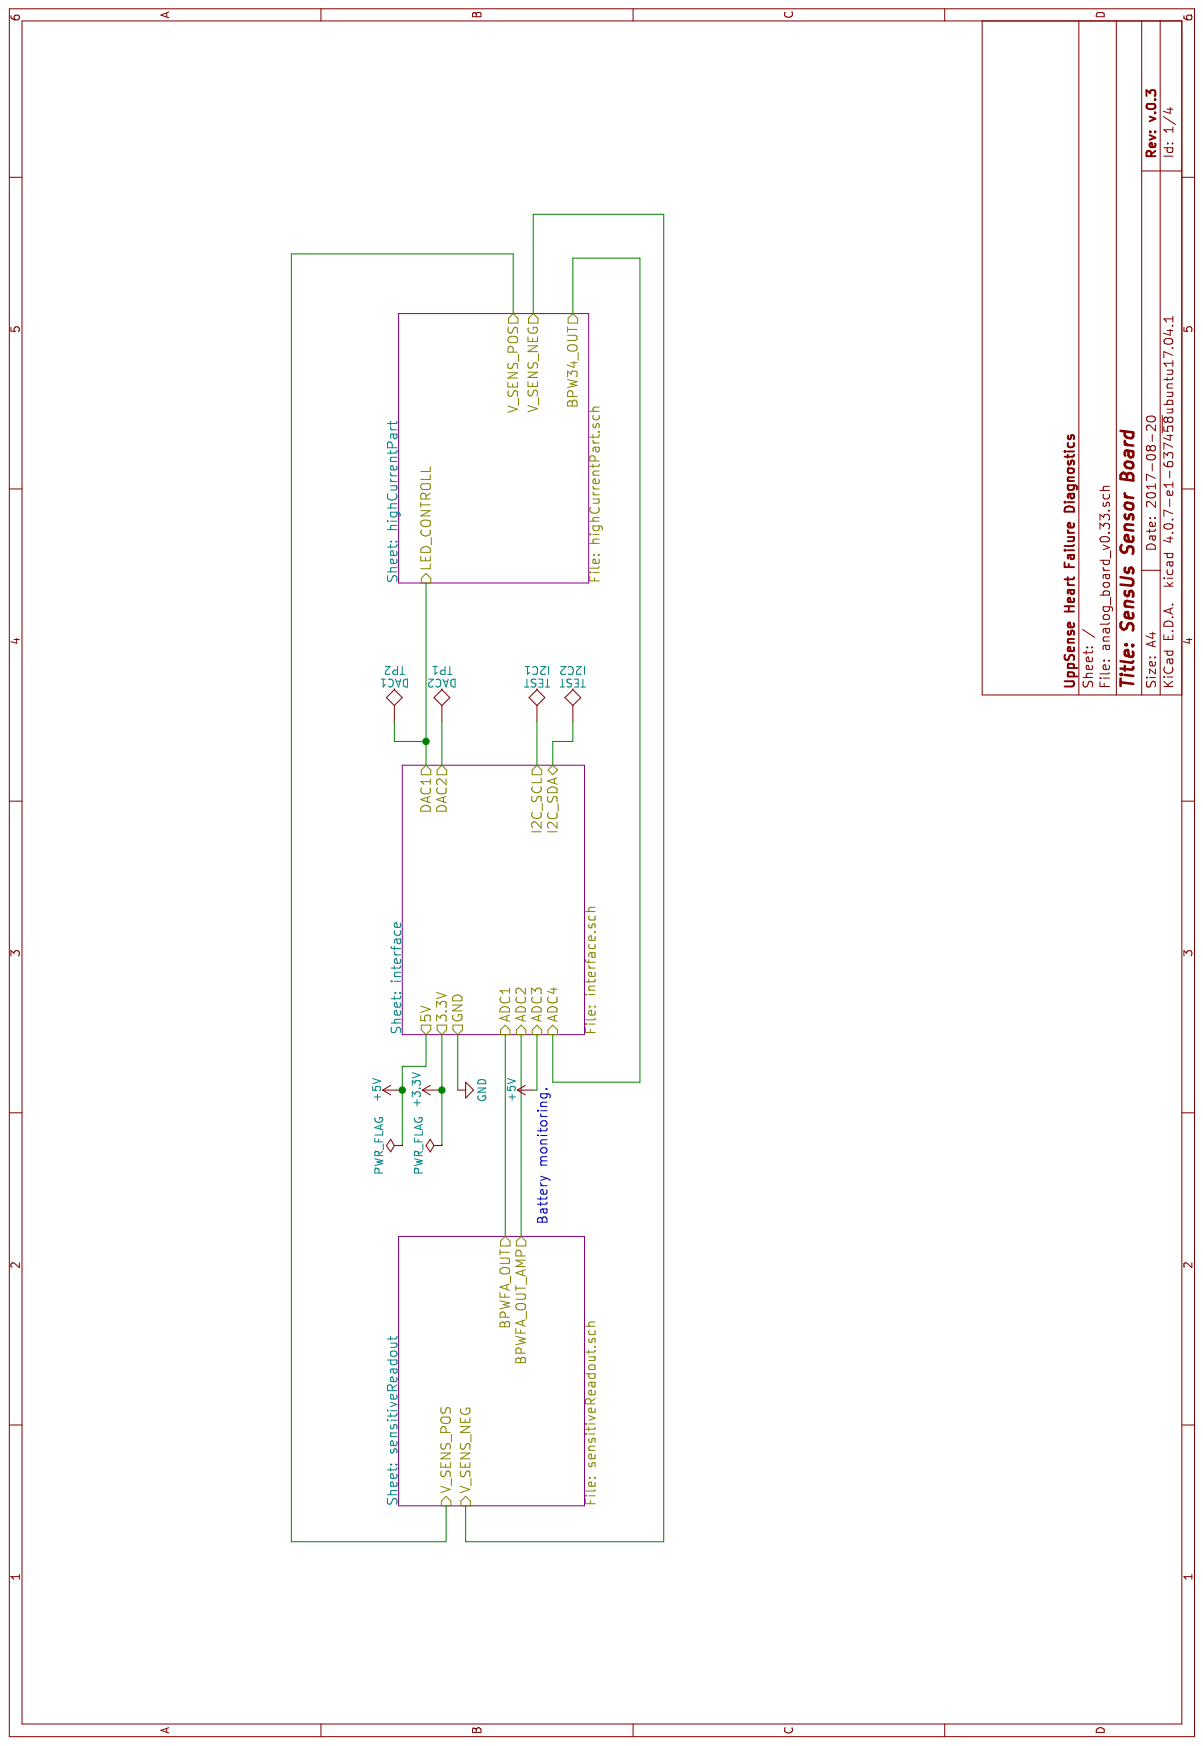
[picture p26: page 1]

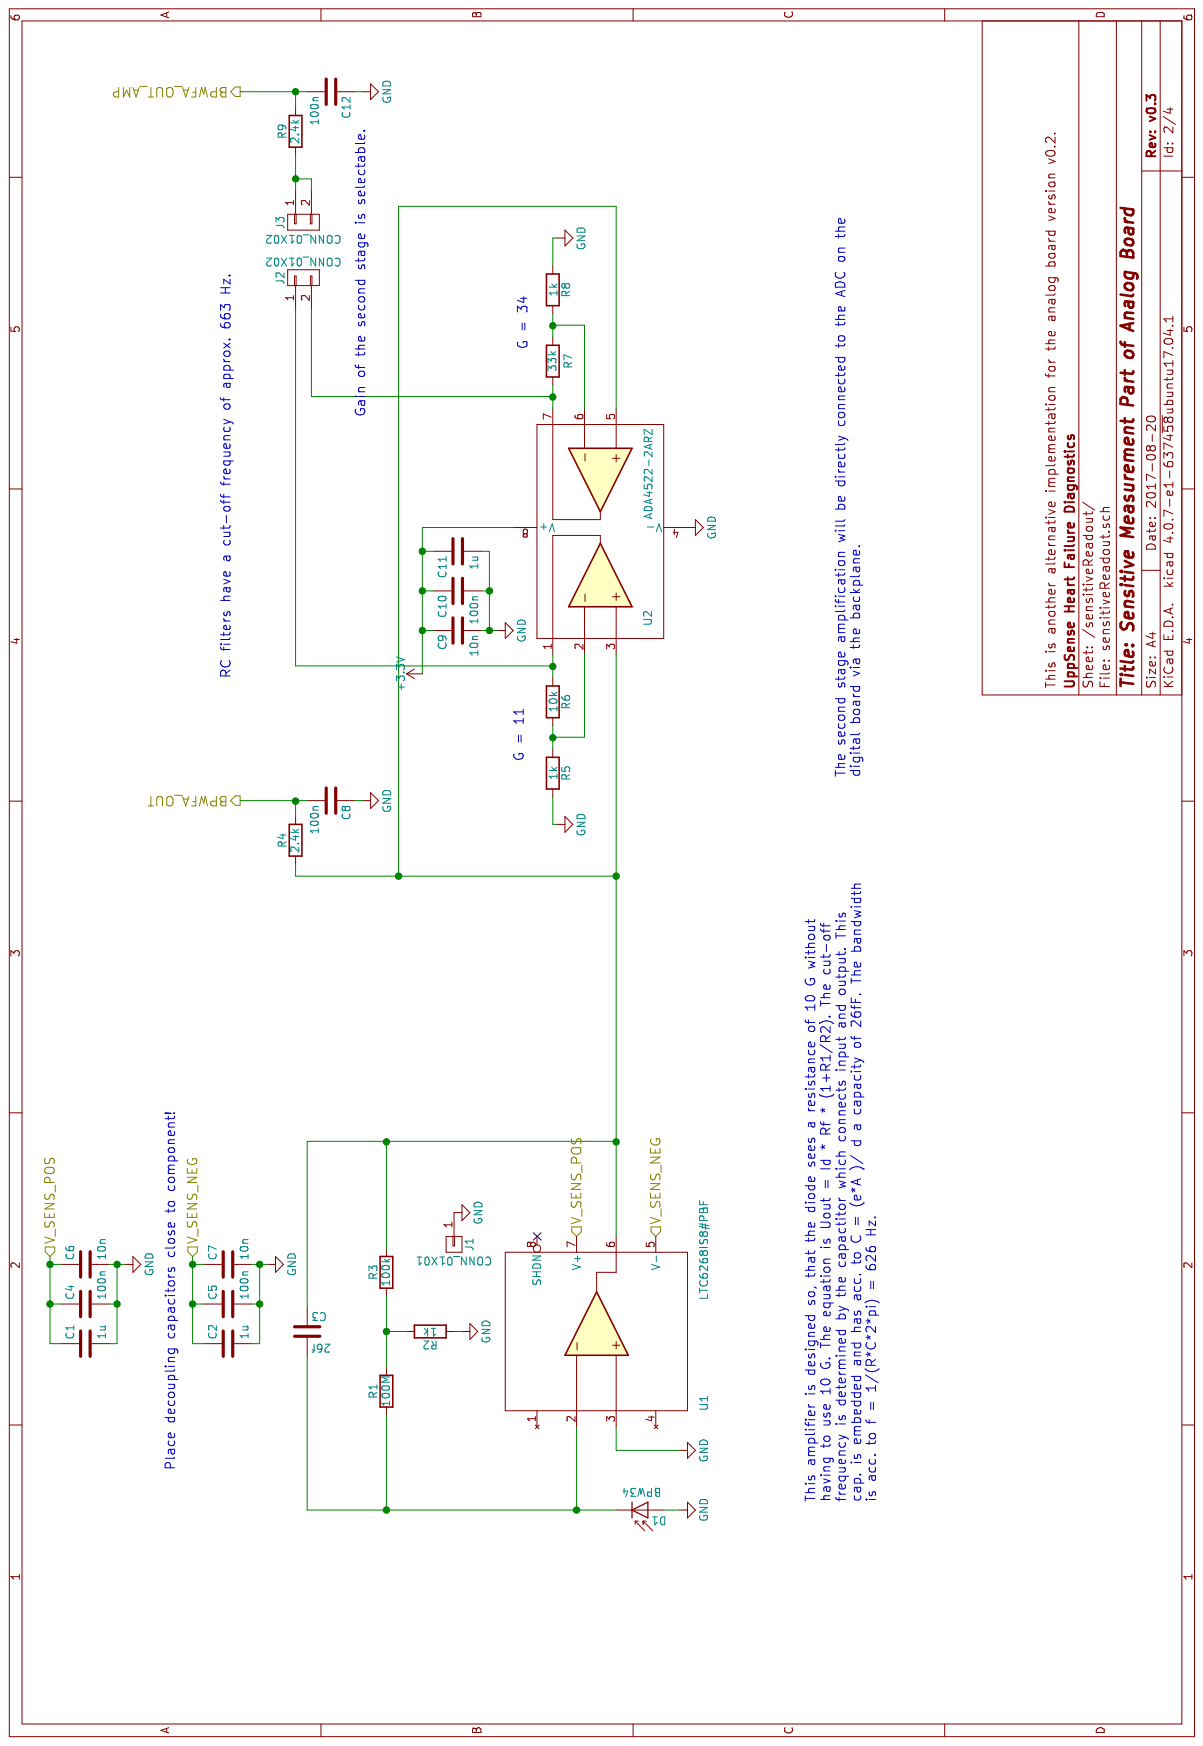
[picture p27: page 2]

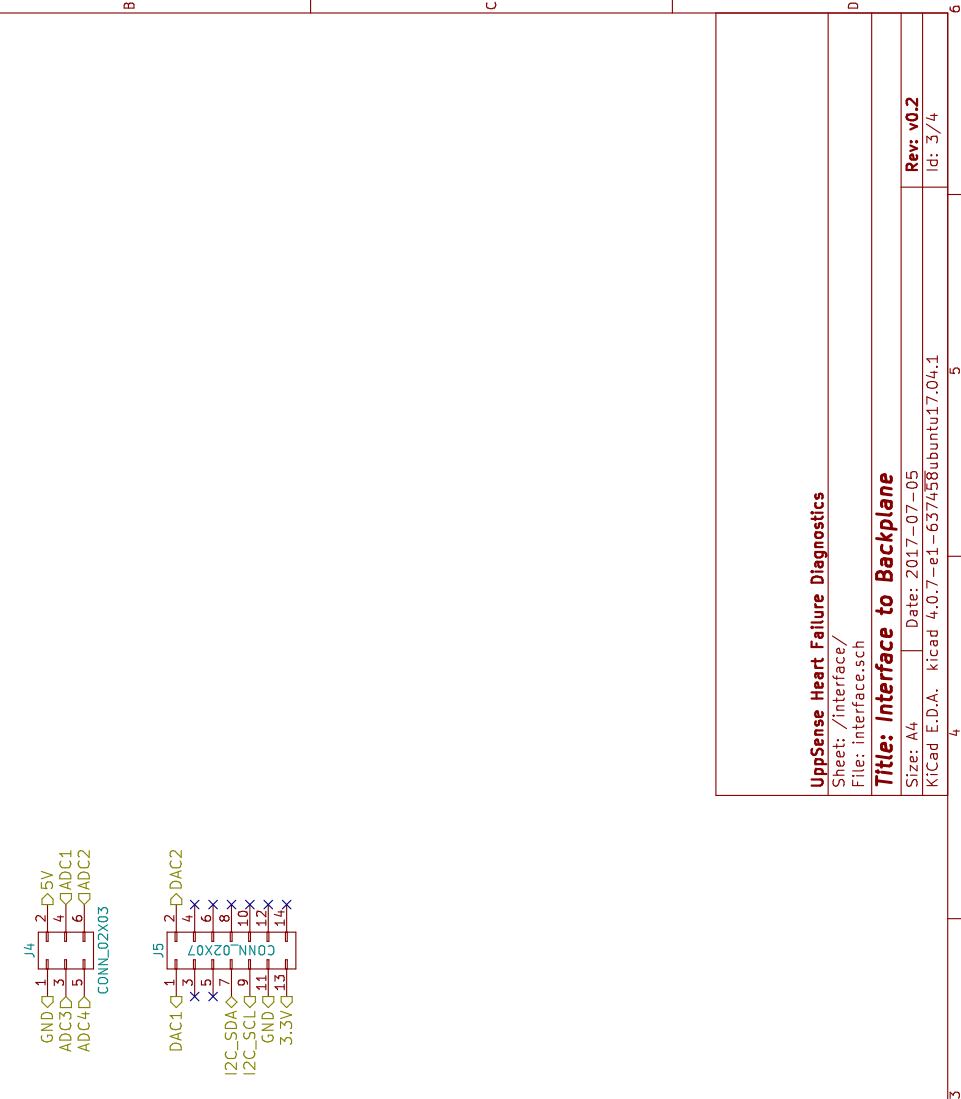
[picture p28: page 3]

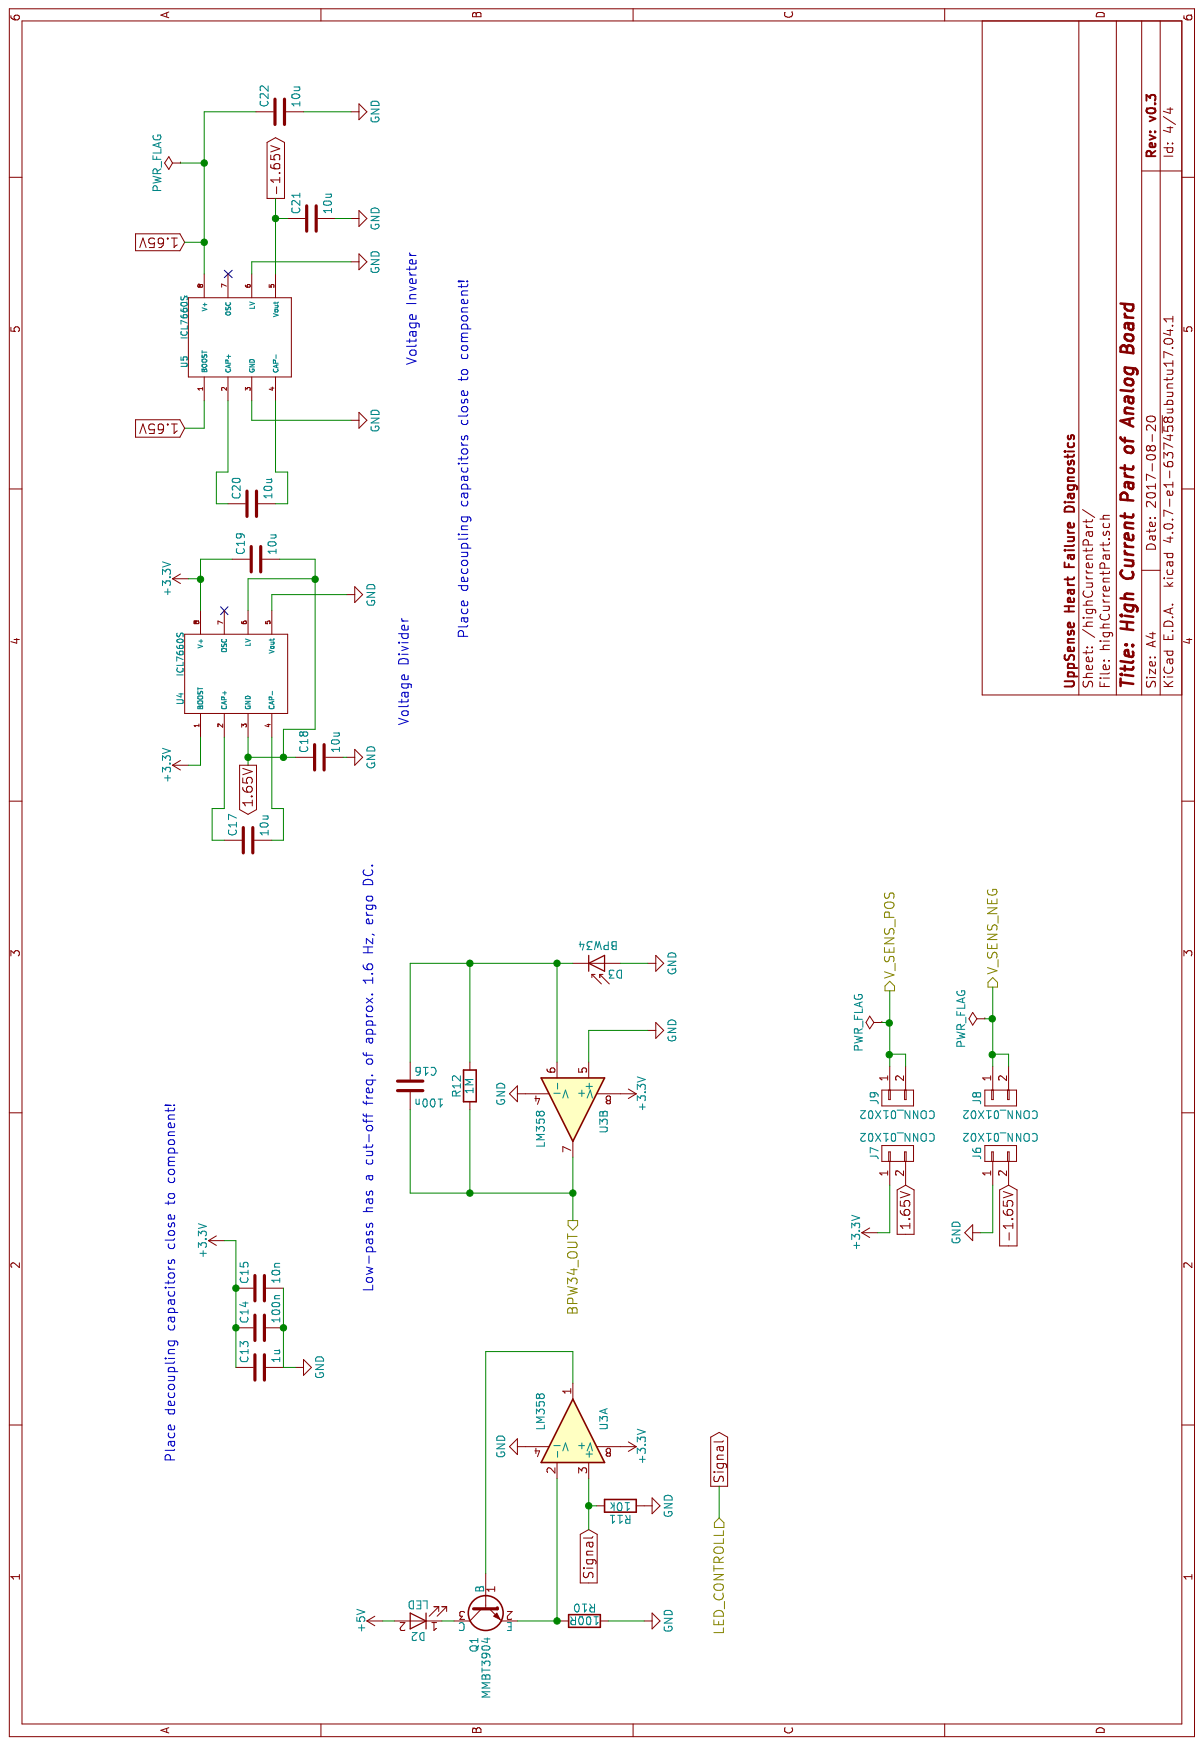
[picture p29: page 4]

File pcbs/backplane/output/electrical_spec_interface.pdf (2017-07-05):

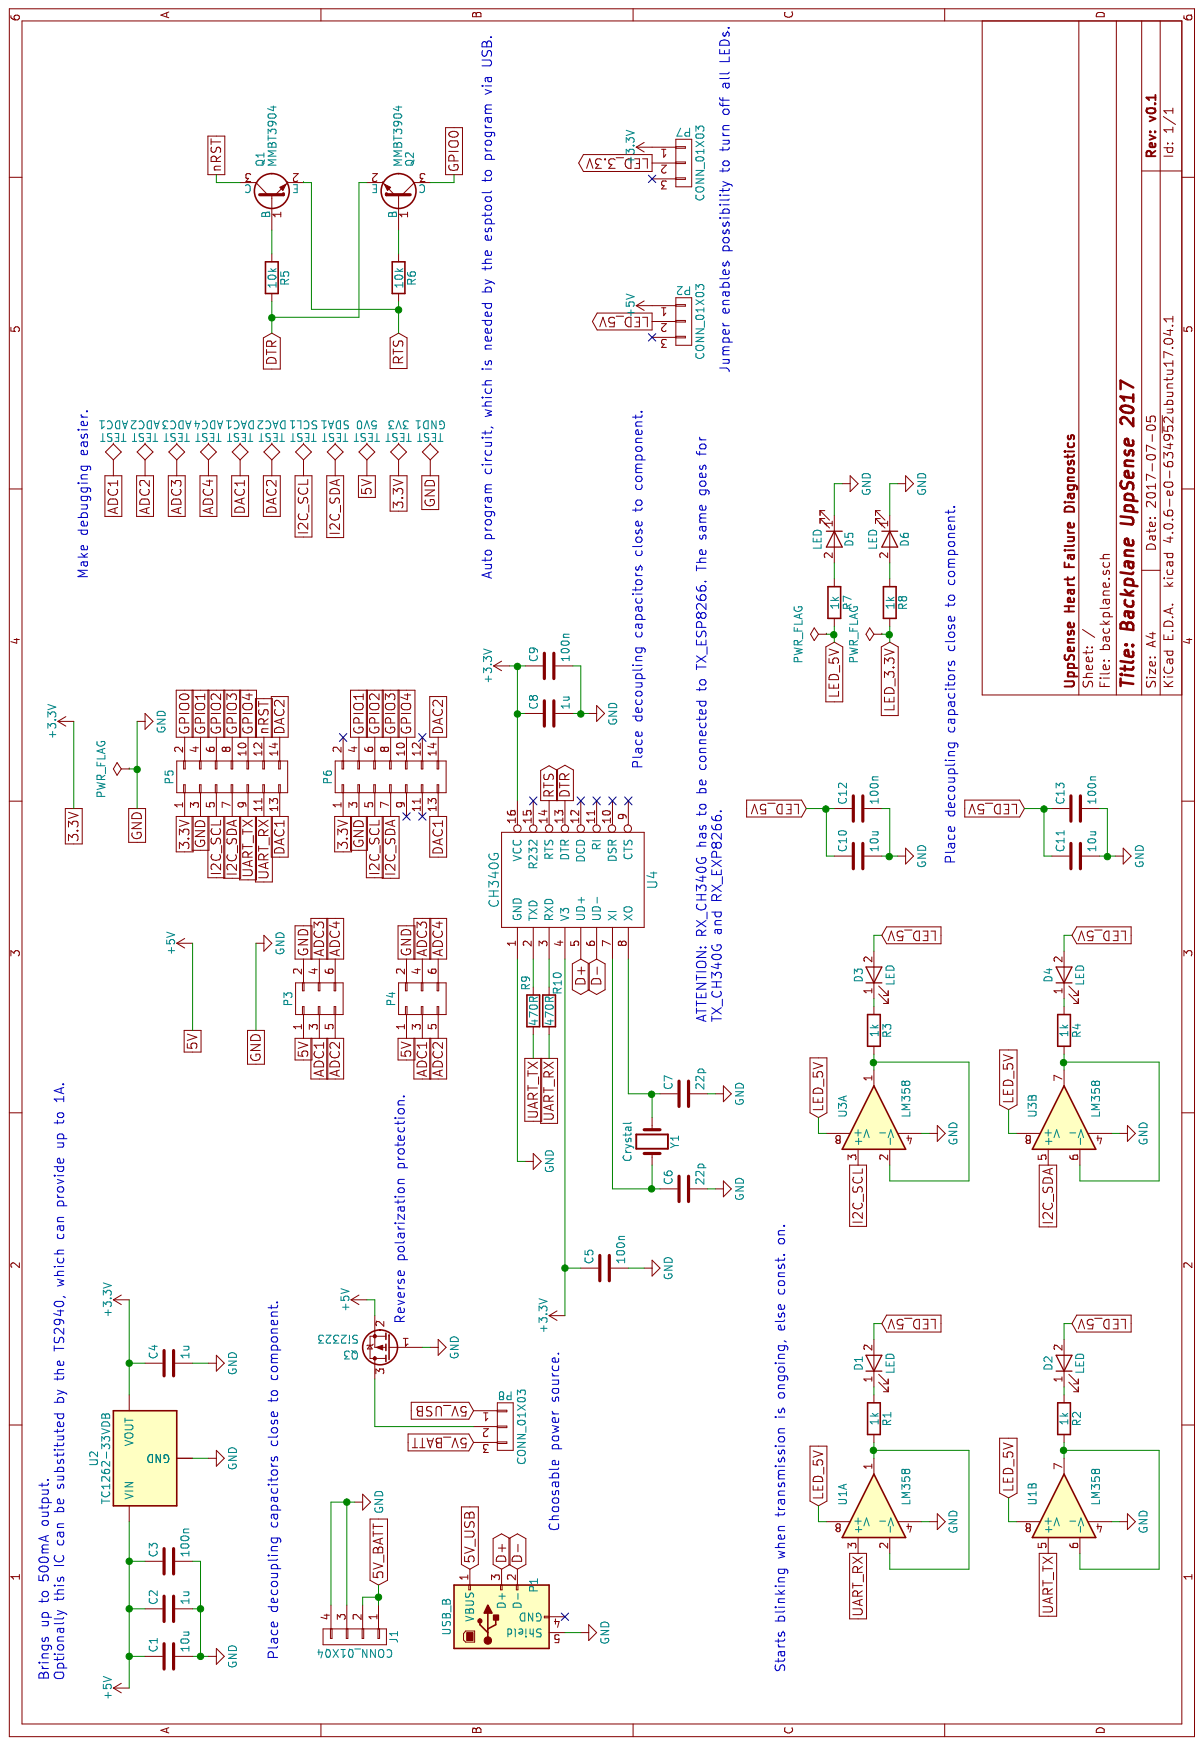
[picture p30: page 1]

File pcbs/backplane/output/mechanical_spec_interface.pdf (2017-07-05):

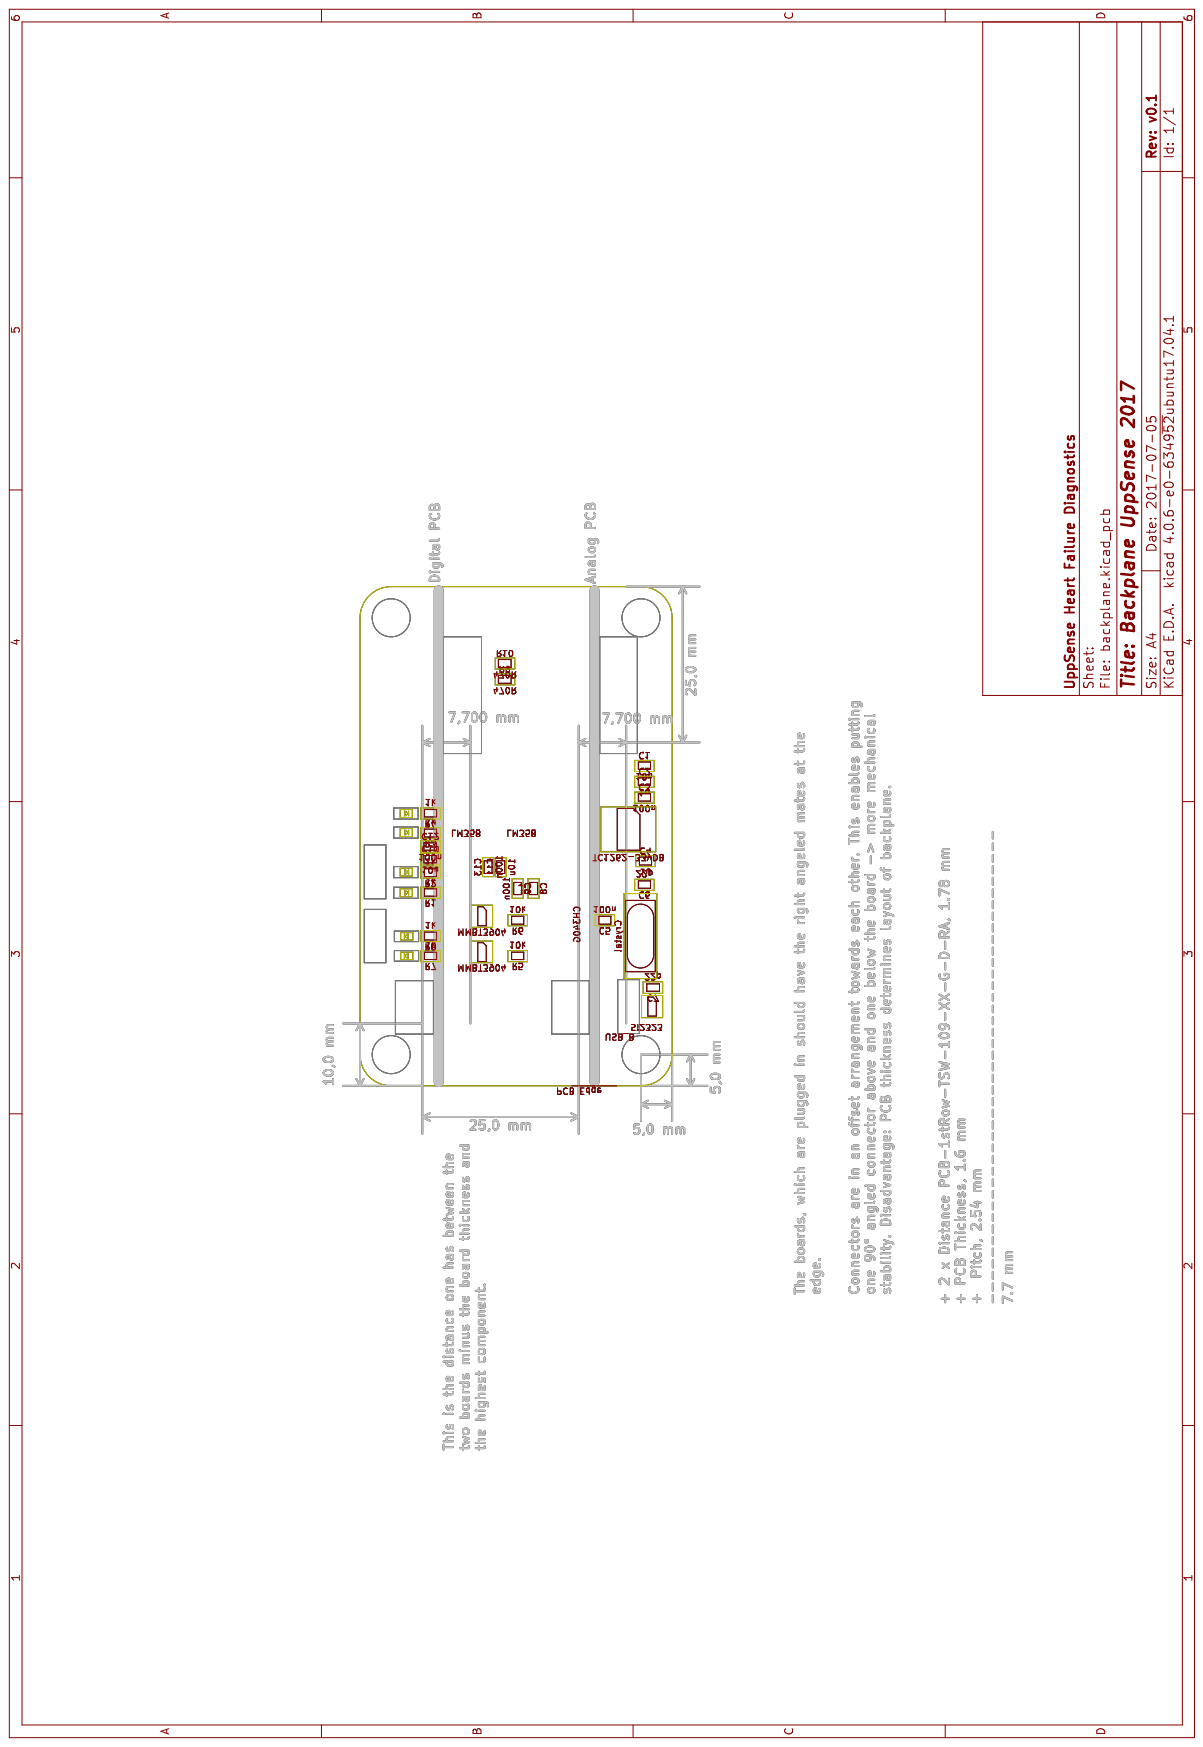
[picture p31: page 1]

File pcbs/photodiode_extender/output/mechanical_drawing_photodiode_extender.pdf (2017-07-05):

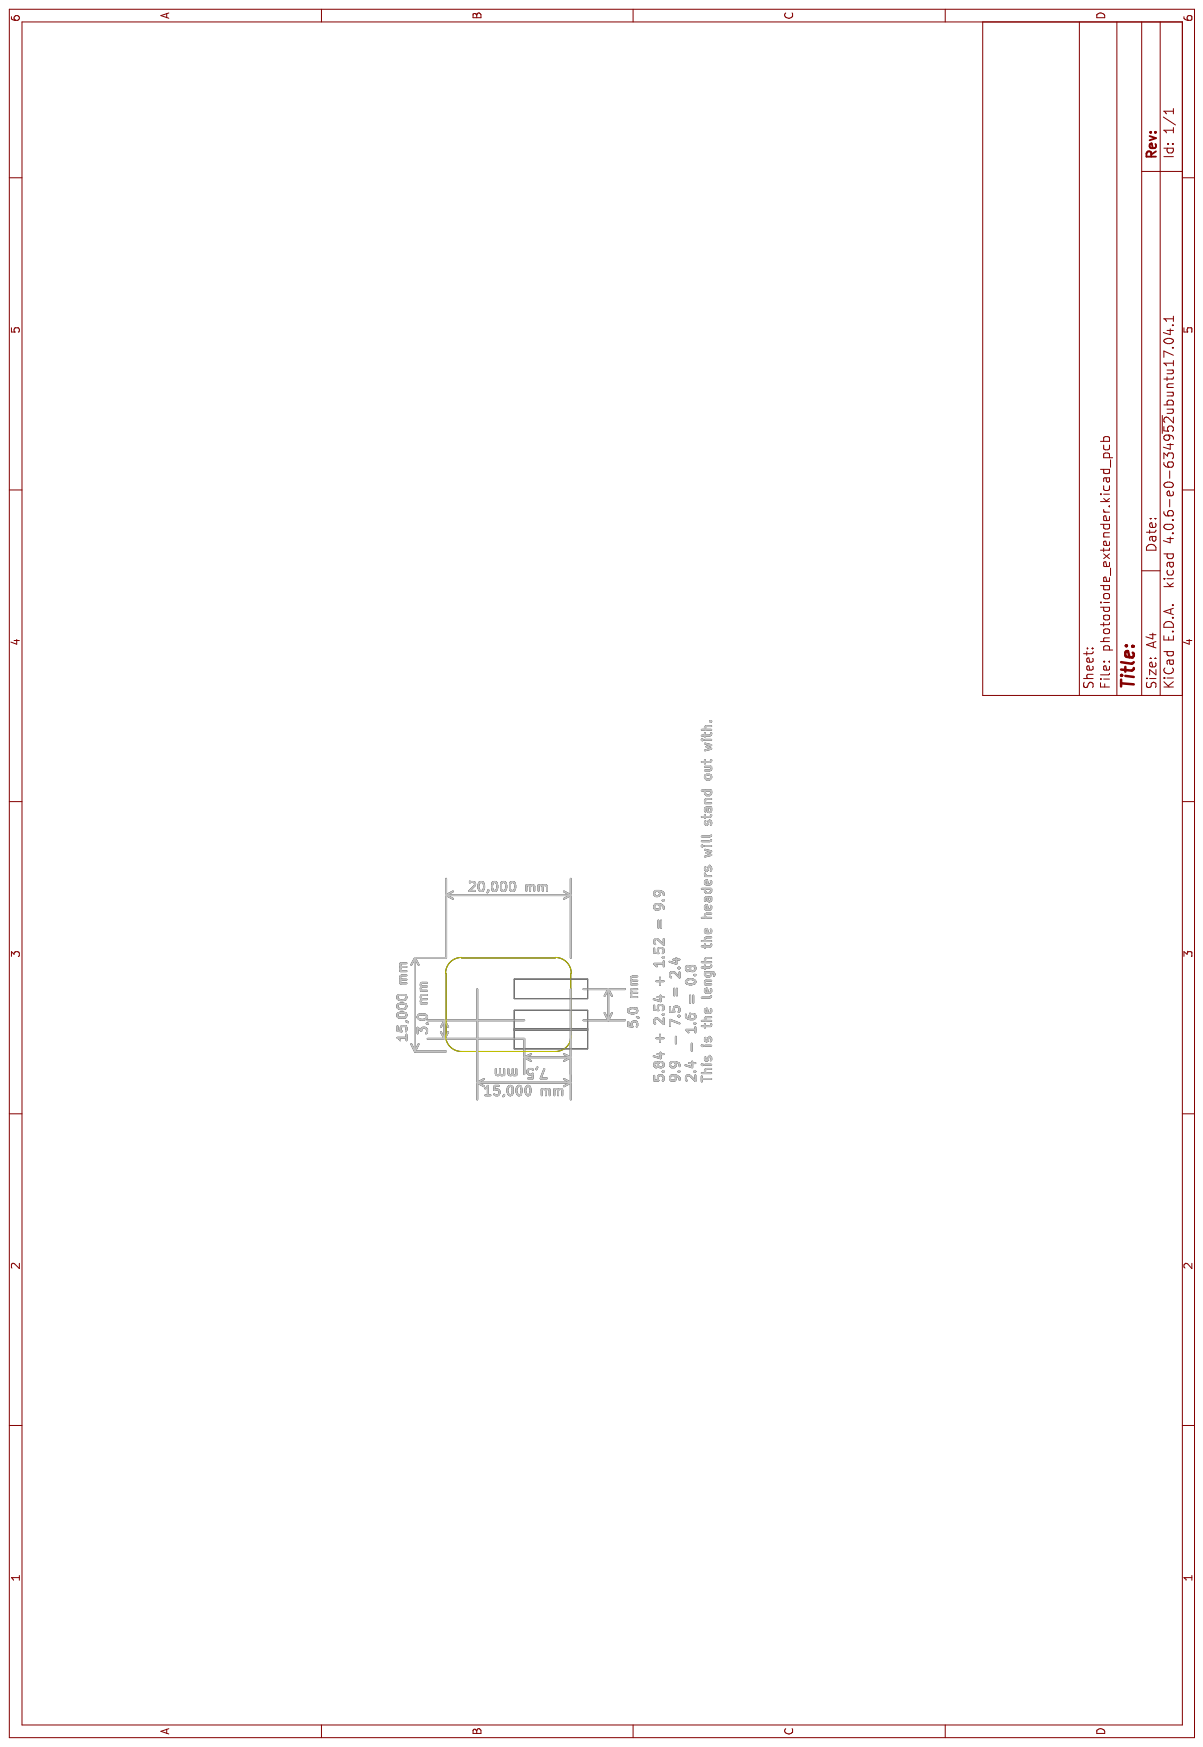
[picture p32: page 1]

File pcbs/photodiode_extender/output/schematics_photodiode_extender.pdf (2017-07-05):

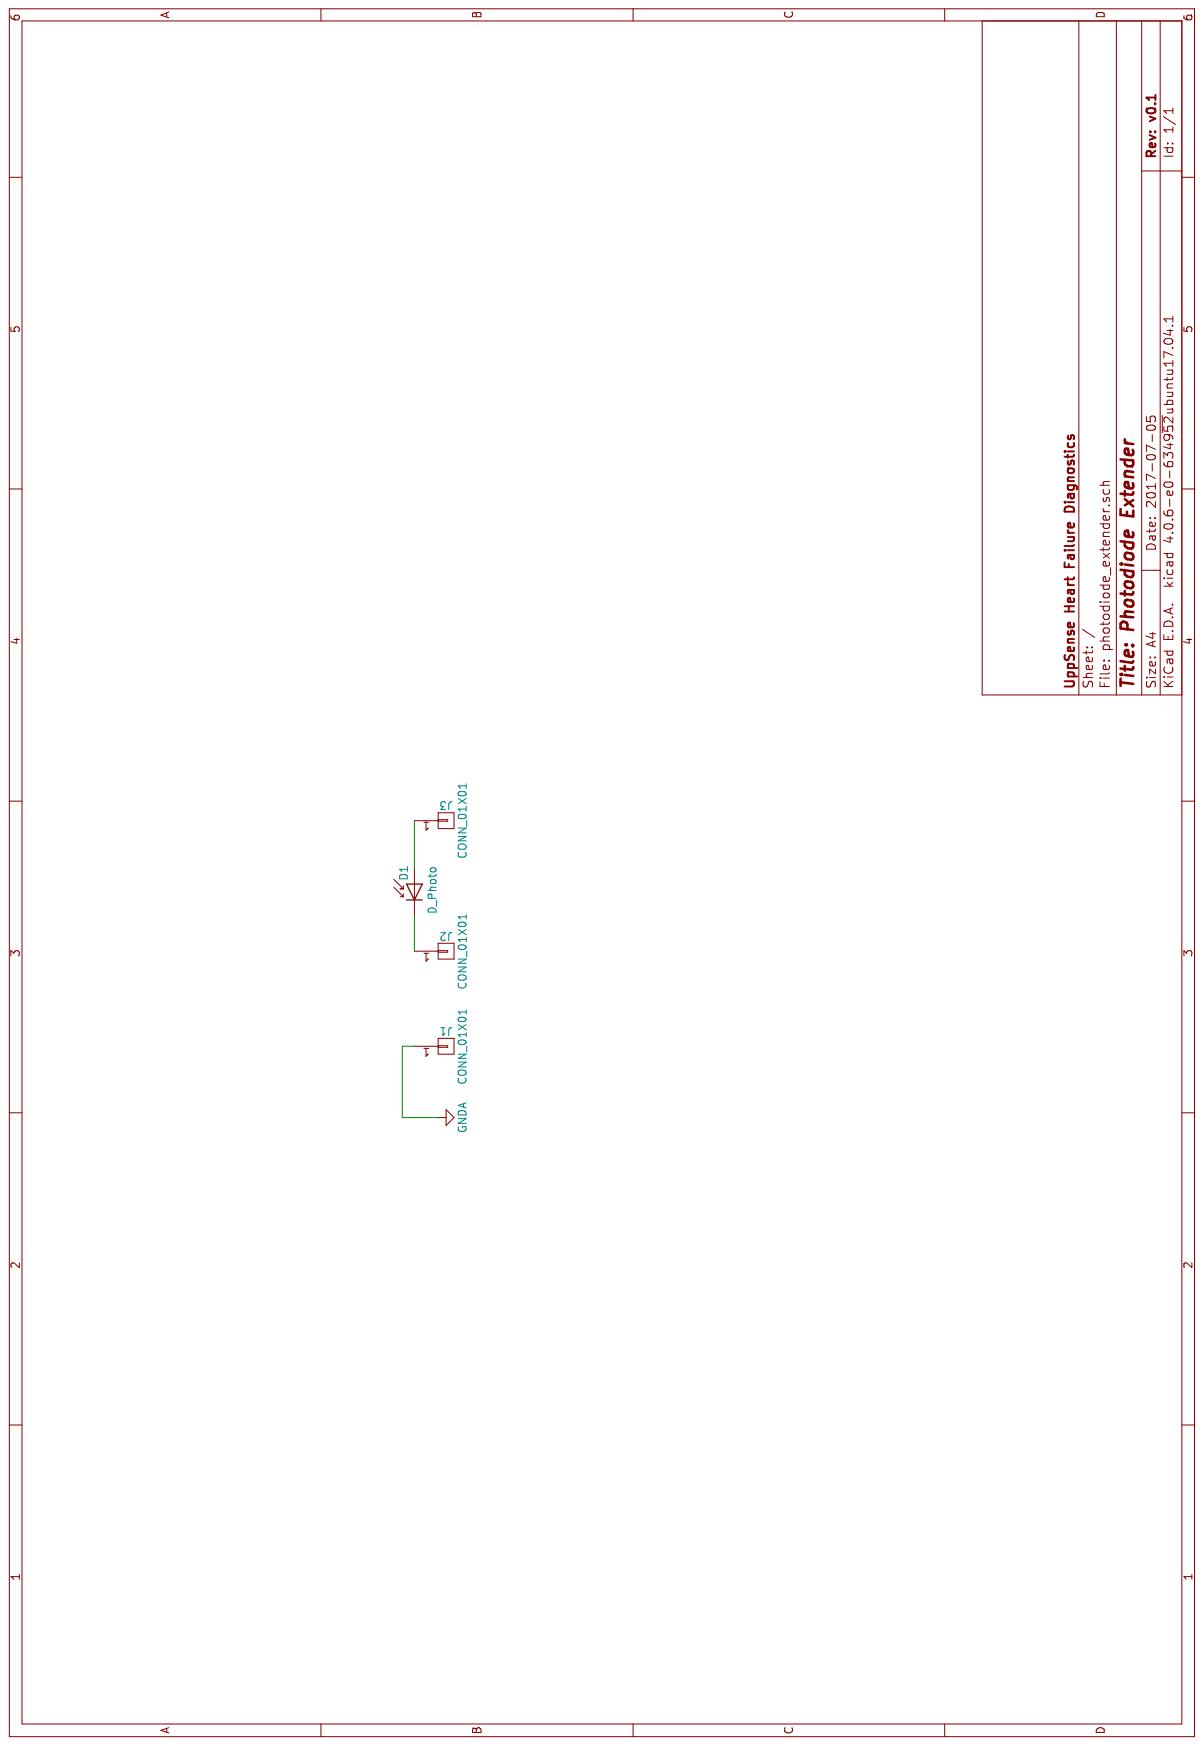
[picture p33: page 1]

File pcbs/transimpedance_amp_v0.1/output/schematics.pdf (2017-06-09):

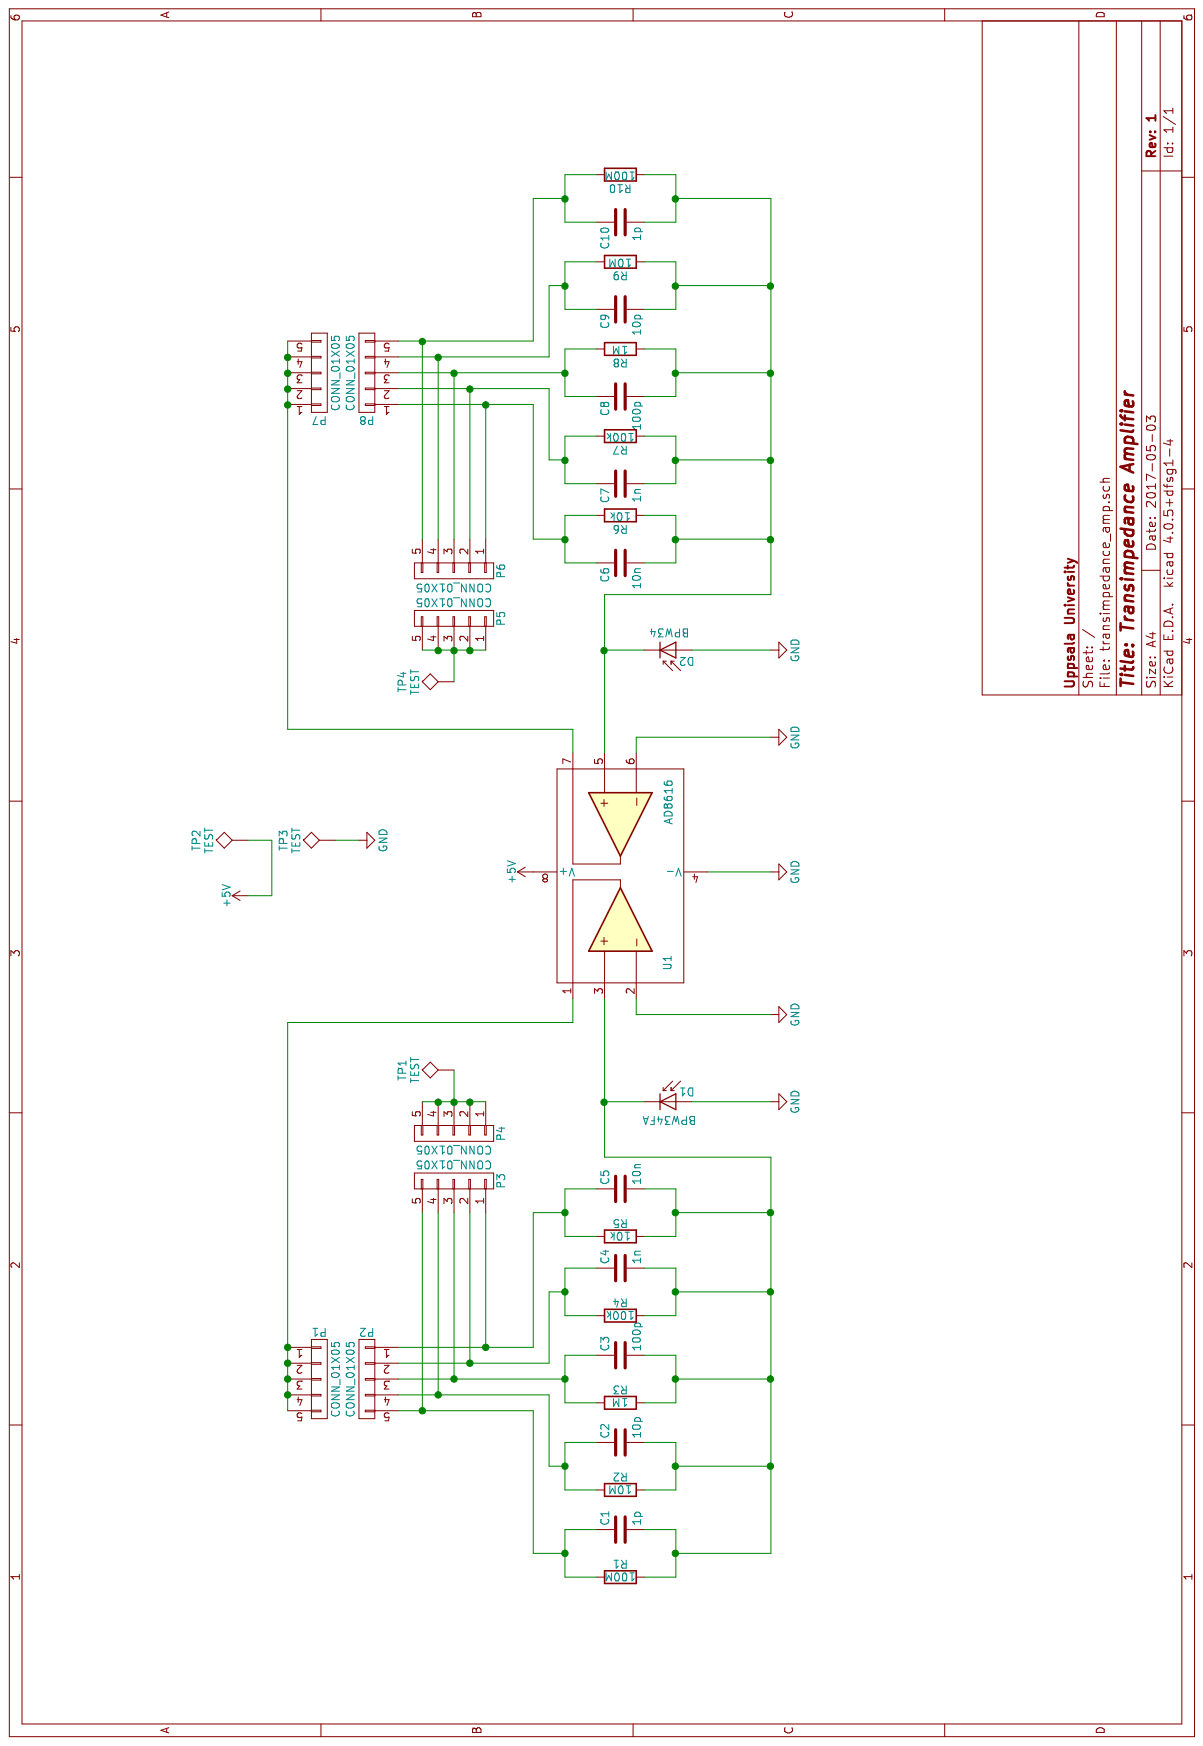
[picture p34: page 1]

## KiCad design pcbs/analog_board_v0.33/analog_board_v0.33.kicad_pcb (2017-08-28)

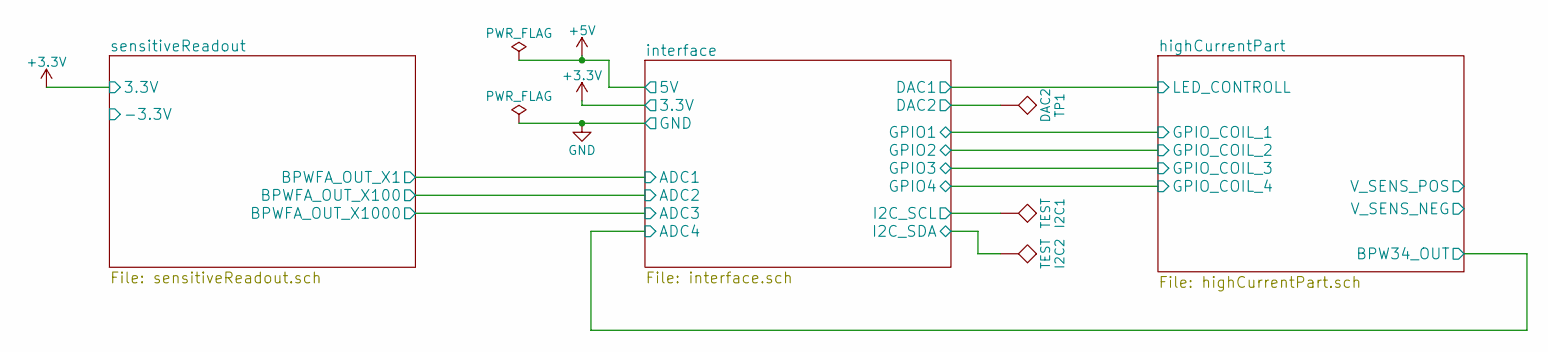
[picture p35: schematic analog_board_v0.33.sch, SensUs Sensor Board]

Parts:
I2C1, I2C2: TEST; TP_SMD_quadr_1mm
TP1: DAC2; TP_SMD_quadr_1mm

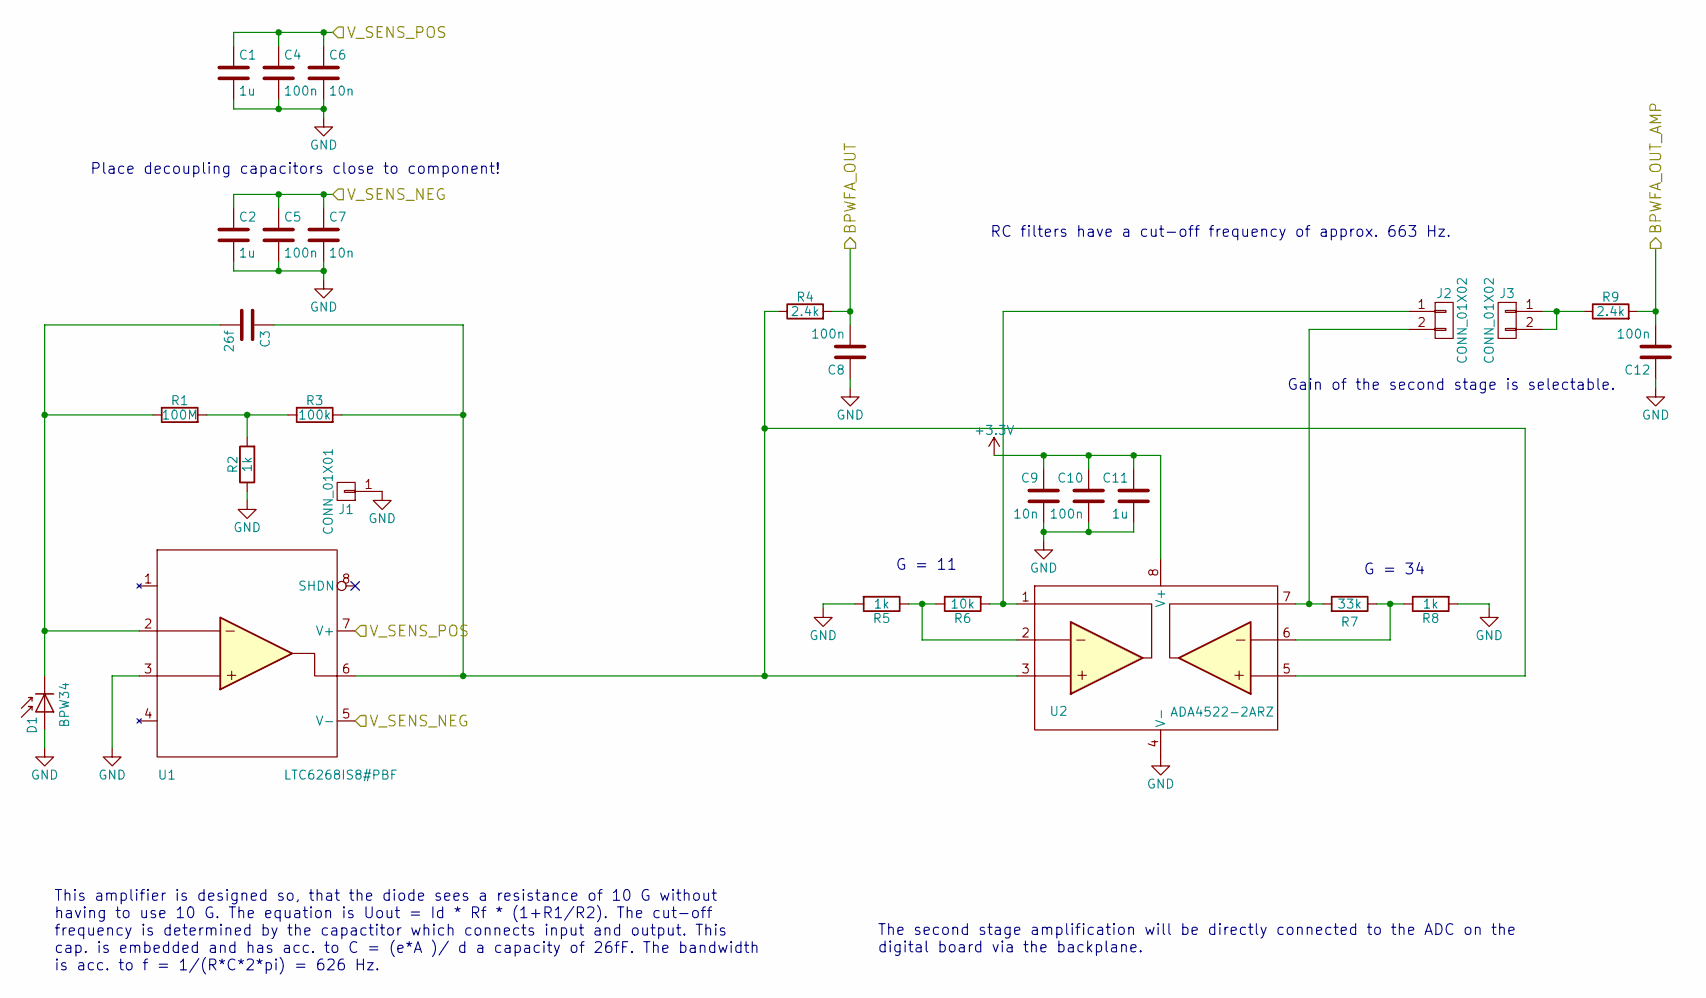
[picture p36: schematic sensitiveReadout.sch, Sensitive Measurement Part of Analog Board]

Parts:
C1, C2, C11: 1u; R_0805; Farnell 2496946
C3: 26f; EMBEDDED_CAP_1mm
C4, C5, C8, C10, C12: 100n; R_0805; Farnell 499687
C6, C7, C9: 10n; R_0805; Farnell 1414662
D1: BPW34; BPW34FA_w_Silks; Farnell 1045425
J1: CONN_01X01; GuardConnector
J2, J3: CONN_01X02; Samtec-PHT-1-2-01-L-S
R1: 100M; R_0805_W_Silks; Farnell 9236511
R2: 1k; R_0805_W_Silks; Farnell 9237496
R3: 100k; R_0805_W_Silks; Farnell 2447551
R4, R9: 2.4k; R_0805; Farnell 2502703
R5, R8: 1k; R_0805; Farnell 9237496
R6: 10k; R_0805; Farnell 9237755
R7: 33k; R_0805; Farnell 2078965
U1: LTC6268IS8#PBF; SOIC-8-N-W-Silks; Farnell 2464182
U2: ADA4522-2ARZ; SOIC-8-N; Farnell 2505560

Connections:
+3V3: C9.1, C10.1, C11.1, U2.8 (V+); also elsewhere on the board
/highCurrentPart/V_SENS_NEG: C2.1, C5.1, C7.1, U1.5 (V-); also elsewhere on the board
/highCurrentPart/V_SENS_POS: C1.1, C4.1, C6.1, U1.7 (V+); also elsewhere on the board
/interface/ADC1: C8.2, R4.2; also elsewhere on the board
/interface/ADC2: C12.2, R9.2; also elsewhere on the board
GND: C1.2, C2.2, C4.2, C5.2, C6.2, C7.2, C8.1, C9.2, C10.2, C11.2, C12.1, D1.2 (A), J1.1, R2.1, R5.2, R8.2, U1.3, U2.4 (V-); also elsewhere on the board
unnamed: C3.1, R3.2, R4.1, U1.6, U2.3, U2.5
unnamed: C3.2, D1.1 (K), R1.1, U1.2
unnamed: J2.1, R6.2, U2.1
unnamed: J2.2, R7.2, U2.7
unnamed: J3.1, J3.2, R9.1
unnamed: R1.2, R2.2, R3.1
unnamed: R5.1, R6.1, U2.2
unnamed: R7.1, R8.1, U2.6

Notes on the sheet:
Place decoupling capacitors close to component!
The second stage amplification will be directly connected to the ADC on the digital board via the backplane.
RC filters have a cut-off frequency of approx. 663 Hz.
This amplifier is designed so, that the diode sees a resistance of 10 G without having to use 10 G. The equation is Uout = Id * Rf * (1+R1/R2). The cut-off frequency is determined by the capactitor which connects input and output. This cap. is embedded and has acc. to C = (e*A )/ d a capacity of 26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
G = 11
G = 34
Gain of the second stage is selectable.

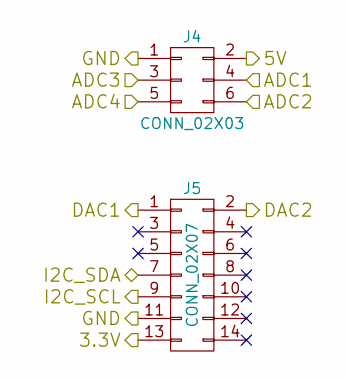
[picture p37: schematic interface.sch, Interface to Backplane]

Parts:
J4: CONN_02X03; Pin_Header_Angled_2x03_Pitch2.54mm
J5: CONN_02X07; Pin_Header_Angled_2x07_Pitch2.54mm

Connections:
+3V3: J5.13; also elsewhere on the board
+5V: J4.2, J4.3; also elsewhere on the board
/interface/ADC1: J4.4; also elsewhere on the board
/interface/ADC2: J4.6; also elsewhere on the board
/interface/ADC4: J4.5; also elsewhere on the board
/interface/DAC2: J5.2; also elsewhere on the board
/interface/I2C_SCL: J5.9; also elsewhere on the board
/interface/I2C_SDA: J5.7; also elsewhere on the board
GND: J4.1, J5.11; also elsewhere on the board
Signal: J5.1; also elsewhere on the board

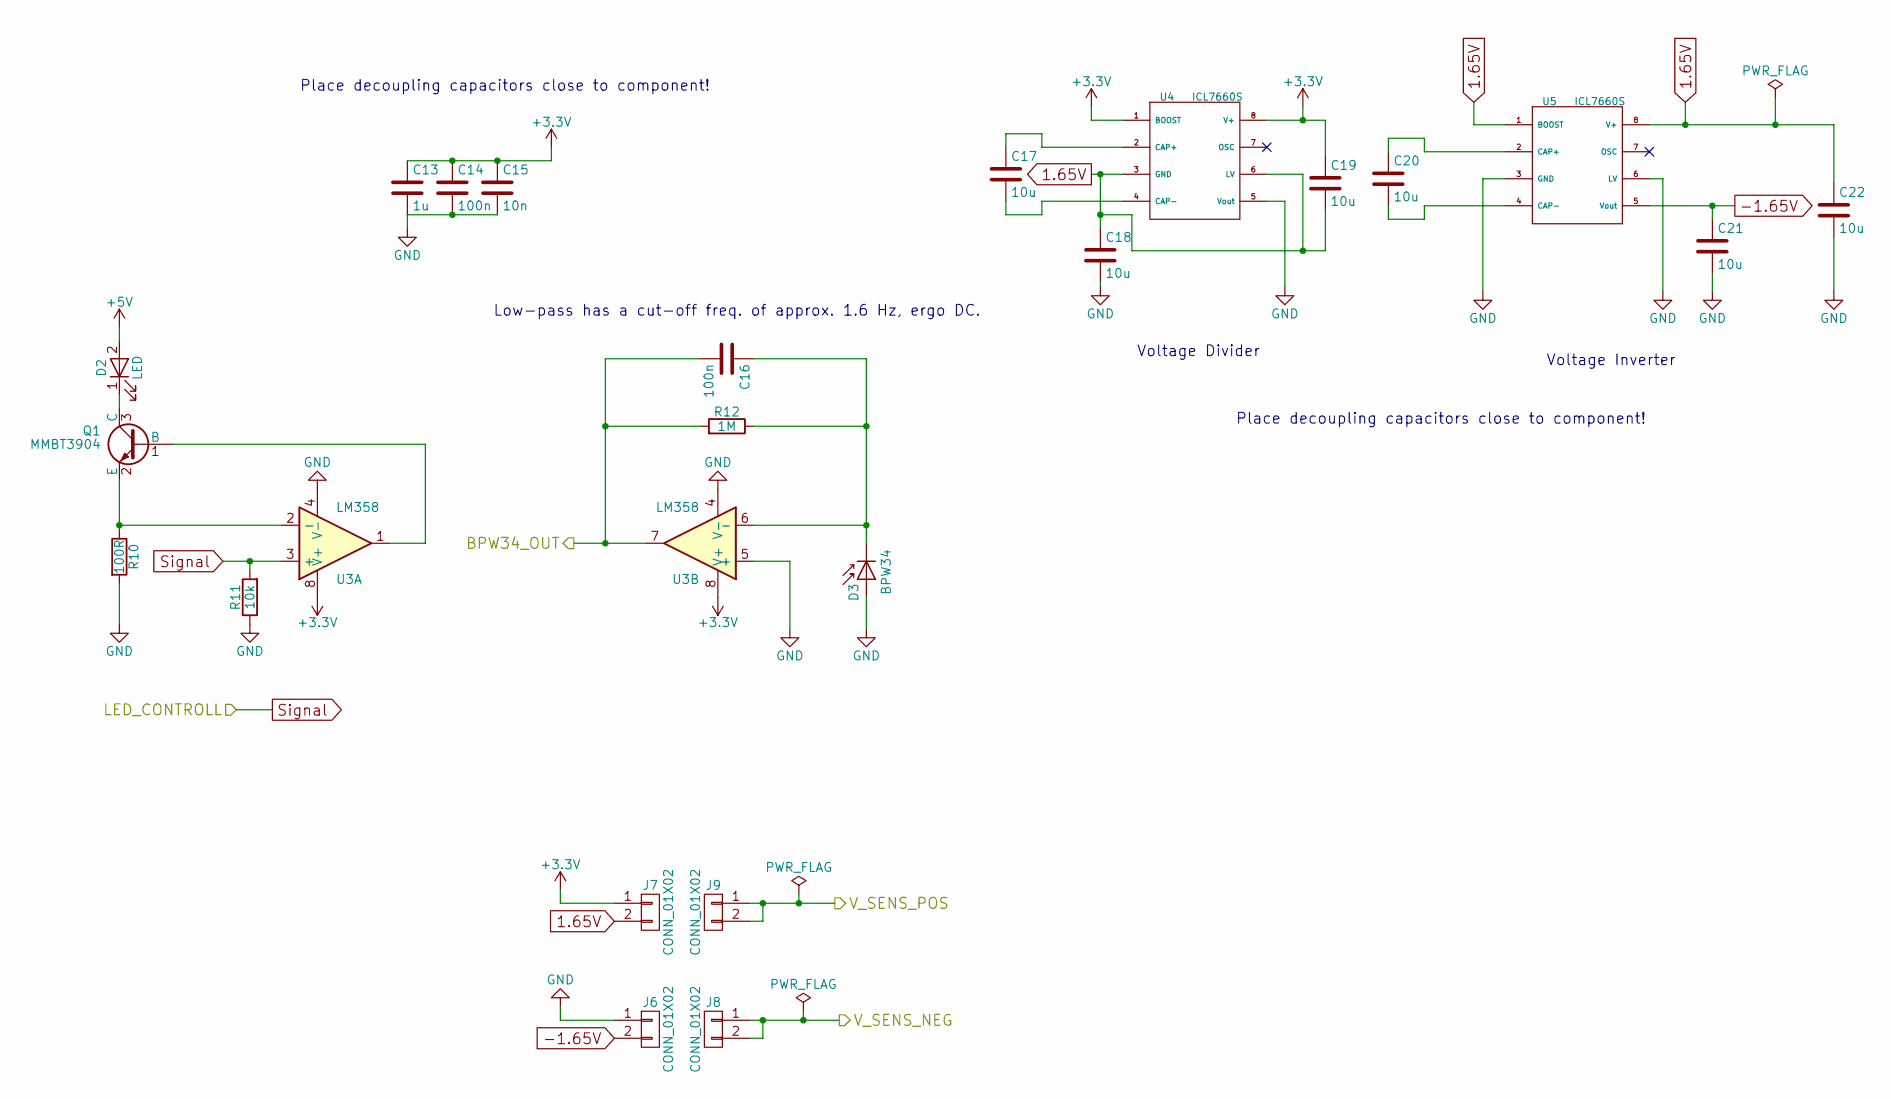
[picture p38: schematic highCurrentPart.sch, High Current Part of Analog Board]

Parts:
C13: 1u; R_0805; Farnell 2496946
C14, C16: 100n; R_0805; Farnell 499687
C15: 10n; R_0805; Farnell 1414662
C17, C18, C19, C20, C21, C22: 10u; R_0805; Farnell 1833812
D2: LED; LED_D5.0mm
D3: BPW34; BPW34FA; Farnell 1045425
J6, J7, J8, J9: CONN_01X02; Samtec-PHT-1-2-01-L-S
Q1: MMBT3904; SOT-23; Farnell 1757935
R10: 100R; R_0805; Farnell 9237364
R11: 10k; R_0805; Farnell 9237755
R12: 1M; R_0805; Farnell 1576507
U3: LM358; SOIC-8-N; Farnell 1564331
U4, U5: ICL7660S; SOIC-8-N; Farnell 1561969

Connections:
1.65V: C18.1, C19.2, C22.1, J7.2, U4.3 (GND), U4.6 (LV), U5.1 (BOOST), U5.8 (V+)
+3V3: C13.1, C14.1, C15.1, C19.1, J7.1, U3.8 (V+), U4.1 (BOOST), U4.8 (V+); also elsewhere on the board
+5V: D2.2 (A); also elsewhere on the board
-1.65V: C21.1, J6.2, U5.5 (Vout)
/highCurrentPart/V_SENS_NEG: J8.1, J8.2; also elsewhere on the board
/highCurrentPart/V_SENS_POS: J9.1, J9.2; also elsewhere on the board
/interface/ADC4: C16.2, R12.2, U3.7; also elsewhere on the board
GND: C13.2, C14.2, C15.2, C18.2, C21.2, C22.2, D3.2 (A), J6.1, R10.2, R11.1, U3.4 (V-), U3.5 (+), U4.5 (Vout), U5.3 (GND), U5.6 (LV); also elsewhere on the board
unnamed: C16.1, D3.1 (K), R12.1, U3.6 (-)
unnamed: C17.1, U4.2 (CAP+)
unnamed: C17.2, U4.4 (CAP-)
unnamed: C20.1, U5.2 (CAP+)
unnamed: C20.2, U5.4 (CAP-)
unnamed: D2.1 (K), Q1.3 (C)
unnamed: Q1.1 (B), U3.1
unnamed: Q1.2 (E), R10.1, U3.2 (-)
Signal: R11.2, U3.3 (+); also elsewhere on the board

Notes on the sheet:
Place decoupling capacitors close to component!
Low-pass has a cut-off freq. of approx. 1.6 Hz, ergo DC.
Voltage Inverter
Voltage Divider

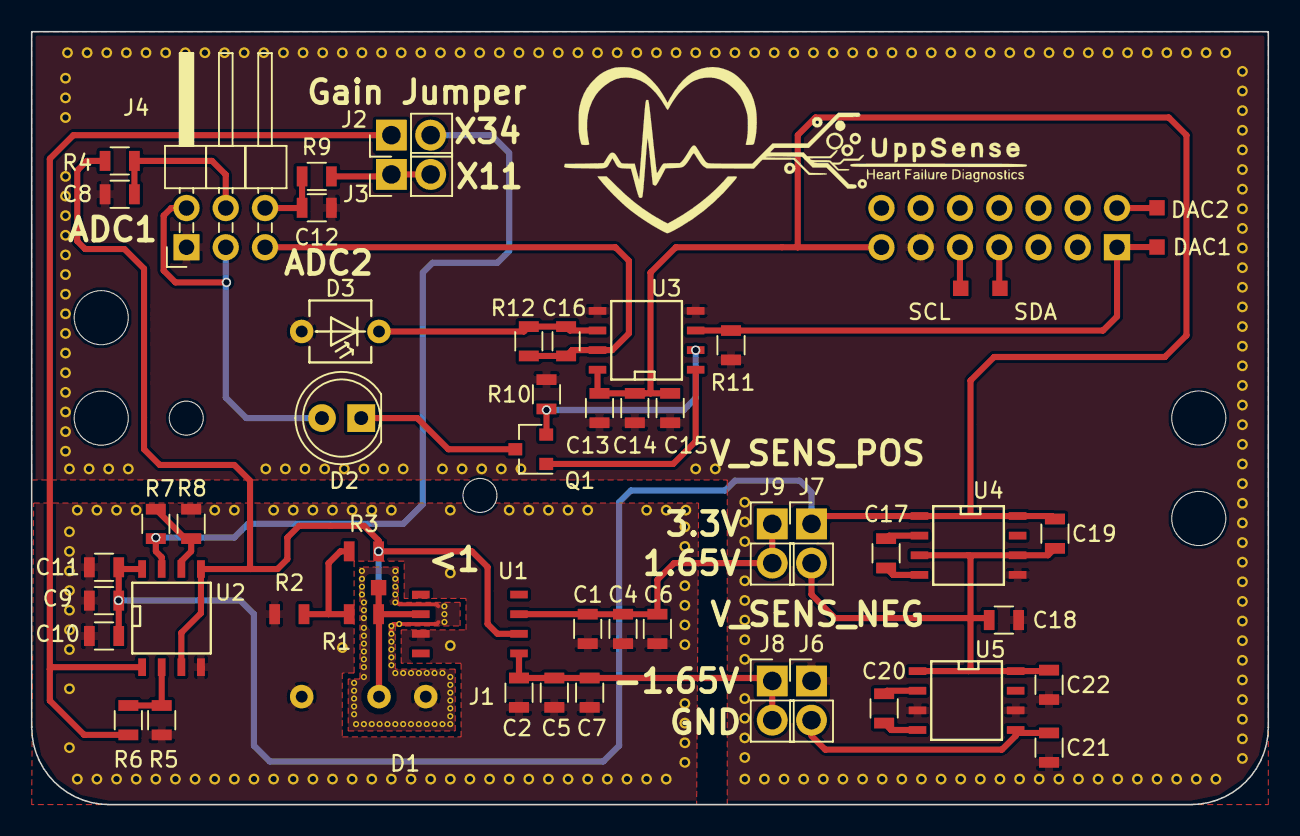
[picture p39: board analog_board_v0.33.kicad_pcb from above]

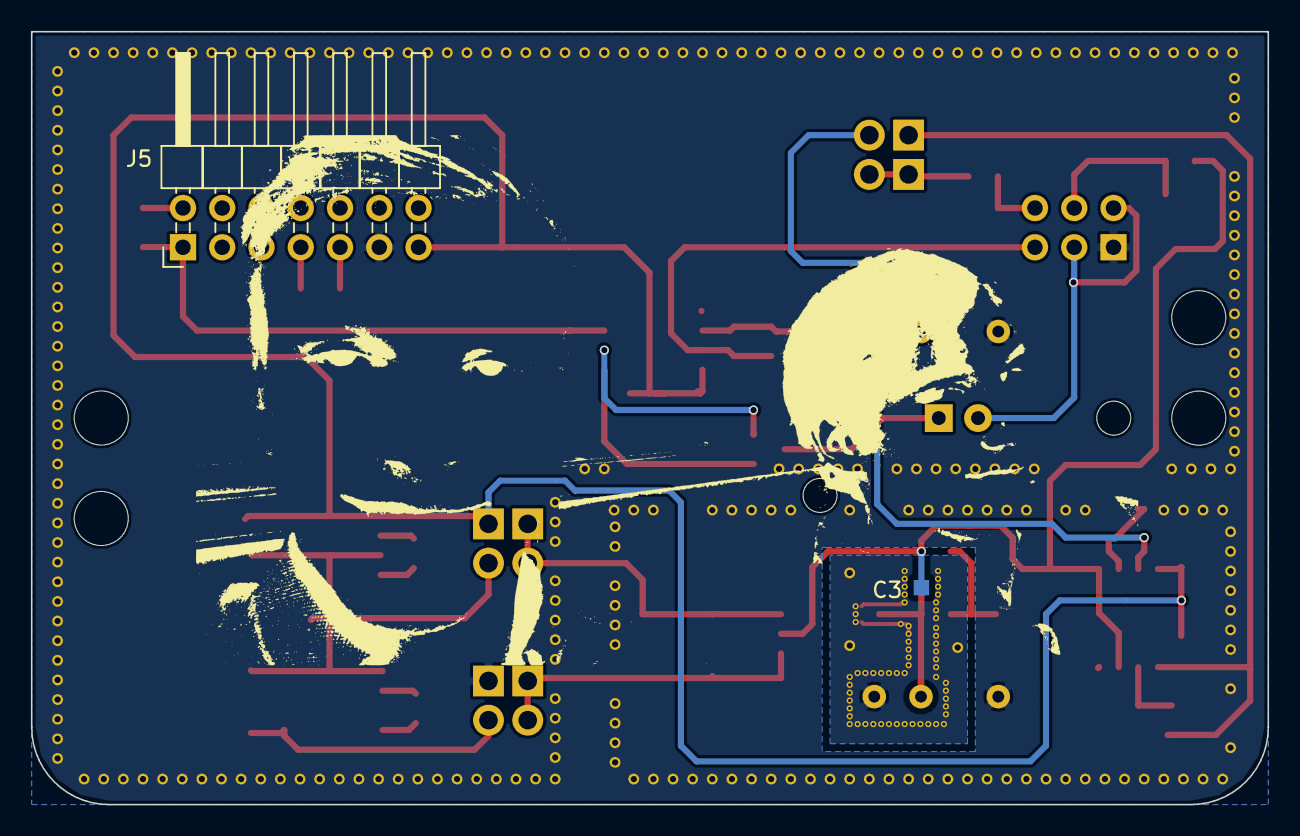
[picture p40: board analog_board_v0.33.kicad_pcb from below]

Board: 2 copper layers, 80.0 x 50.0 mm, 56 parts (2 on the bottom side), 30 nets.

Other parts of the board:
DAC1: DAC1; TP_SMD_quadr_1mm
DAC2: DAC2; TP_SMD_quadr_1mm
SCL: TEST; TP_SMD_quadr_1mm
SDA: TEST; TP_SMD_quadr_1mm

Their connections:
/interface/DAC2: DAC2.1; also elsewhere on the board
/interface/I2C_SCL: SCL.1; also elsewhere on the board
/interface/I2C_SDA: SDA.1; also elsewhere on the board
Signal: DAC1.1; also elsewhere on the board

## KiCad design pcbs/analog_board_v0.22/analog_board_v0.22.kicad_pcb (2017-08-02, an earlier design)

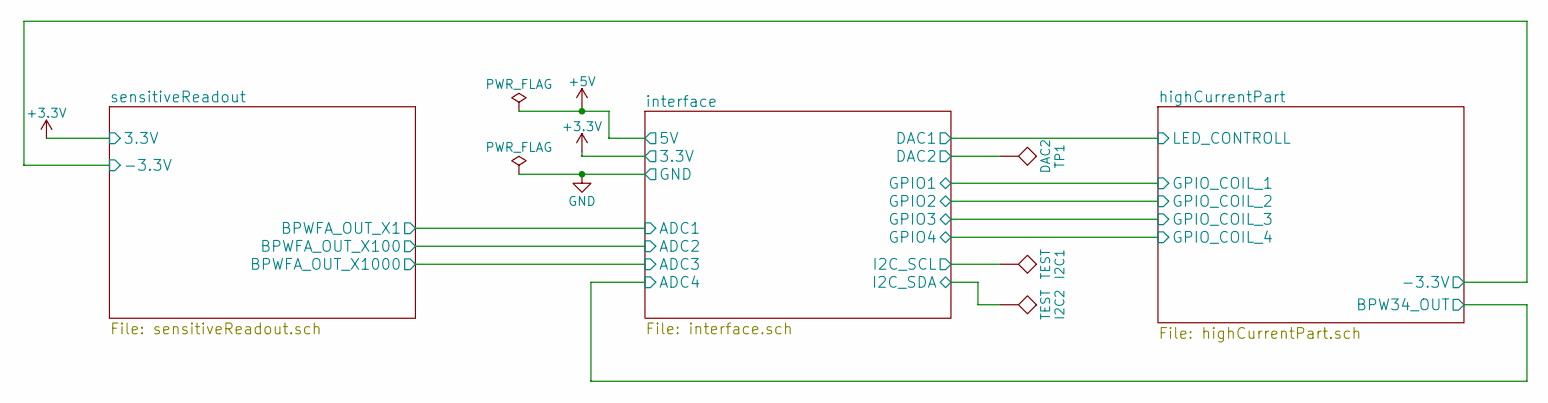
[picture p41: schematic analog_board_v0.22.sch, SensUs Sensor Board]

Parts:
I2C1, I2C2: TEST; TP_SMD_quadr_1mm
TP1: DAC2; TP_SMD_quadr_1mm

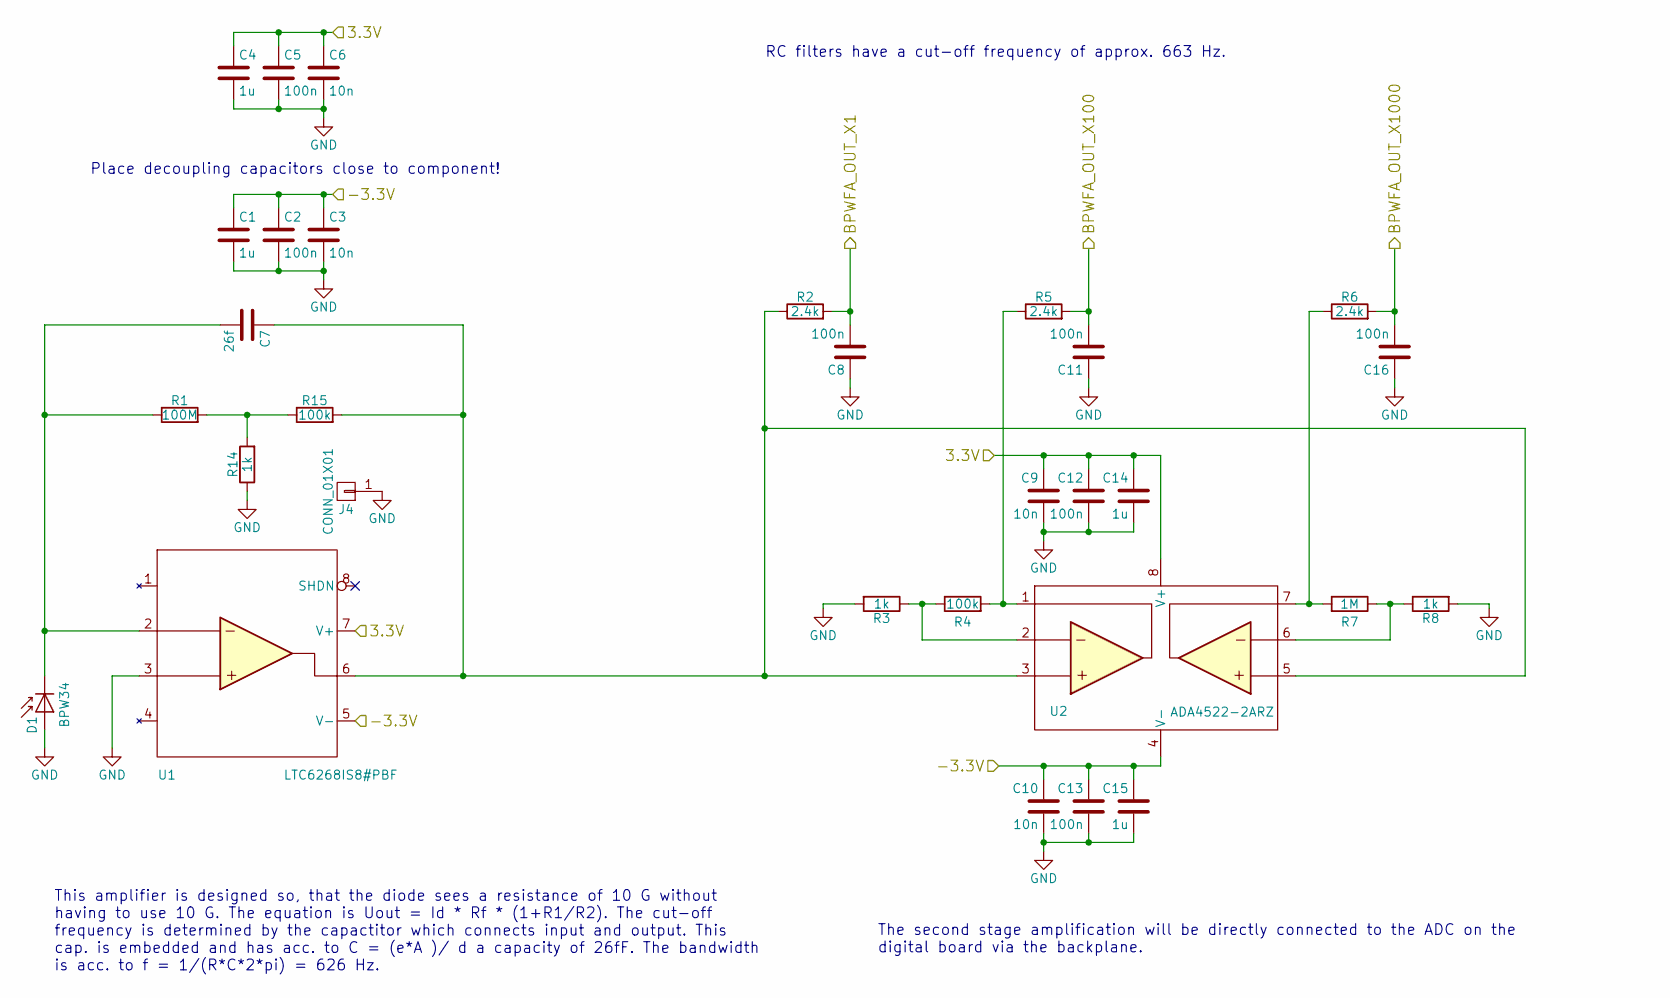
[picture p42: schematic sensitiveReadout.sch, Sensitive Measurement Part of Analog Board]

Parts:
C1, C4, C14, C15: 1u; R_0805; Farnell 2496946
C2, C5, C8, C11, C12, C13, C16: 100n; R_0805; Farnell 499687
C3, C6, C9, C10: 10n; R_0805; Farnell 1414662
C7: 26f; EMBEDDED_CAP_1mm
D1: BPW34; BPW34FA_w_Silks; Farnell 1045425
J4: CONN_01X01; GuardConnector
R1: 100M; R_0805_W_Silks; Farnell 9236511
R2, R5, R6: 2.4k; R_0805; Farnell 2502703
R3, R8: 1k; R_0805; Farnell 9237496
R4: 100k; R_0805; Farnell 2447551
R7: 1M; R_0805; Farnell 1576507
R14: 1k; R_0805_W_Silks; Farnell 9237496
R15: 100k; R_0805_W_Silks; Farnell 2447551
U1: LTC6268IS8#PBF; SOIC-8-N-W-Silks; Farnell 2464182
U2: ADA4522-2ARZ; SOIC-8-N; Farnell 2505560

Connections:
+3V3: C4.1, C5.1, C6.1, C9.1, C12.1, C14.1, U1.7 (V+), U2.8 (V+); also elsewhere on the board
/highCurrentPart/-3.3V: C1.1, C2.1, C3.1, C10.1, C13.1, C15.1, U1.5 (V-), U2.4 (V-); also elsewhere on the board
/interface/ADC1: C8.2, R2.2; also elsewhere on the board
/interface/ADC2: C11.2, R5.2; also elsewhere on the board
/interface/ADC3: C16.2, R6.2; also elsewhere on the board
GND: C1.2, C2.2, C3.2, C4.2, C5.2, C6.2, C8.1, C9.2, C10.2, C11.1, C12.2, C13.2, C14.2, C15.2, C16.1, D1.2 (A), J4.1, R3.2, R8.2, R14.1, U1.3; also elsewhere on the board
unnamed: C7.1, R2.1, R15.2, U1.6, U2.3, U2.5
unnamed: C7.2, D1.1 (K), R1.1, U1.2
unnamed: R1.2, R14.2, R15.1
unnamed: R3.1, R4.1, U2.2
unnamed: R4.2, R5.1, U2.1
unnamed: R6.1, R7.2, U2.7
unnamed: R7.1, R8.1, U2.6

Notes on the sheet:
Place decoupling capacitors close to component!
The second stage amplification will be directly connected to the ADC on the digital board via the backplane.
RC filters have a cut-off frequency of approx. 663 Hz.
This amplifier is designed so, that the diode sees a resistance of 10 G without having to use 10 G. The equation is Uout = Id * Rf * (1+R1/R2). The cut-off frequency is determined by the capactitor which connects input and output. This cap. is embedded and has acc. to C = (e*A )/ d a capacity of 26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

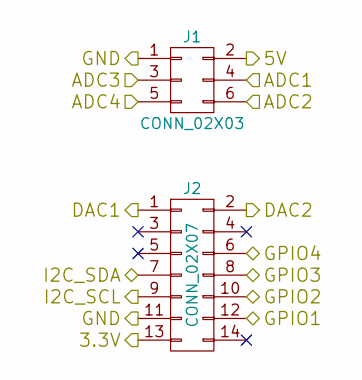
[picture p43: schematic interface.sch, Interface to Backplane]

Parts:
J1: CONN_02X03; Pin_Header_Angled_2x03_Pitch2.54mm
J2: CONN_02X07; Pin_Header_Angled_2x07_Pitch2.54mm

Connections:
+3V3: J2.13; also elsewhere on the board
+5V: J1.2; also elsewhere on the board
/interface/ADC1: J1.4; also elsewhere on the board
/interface/ADC2: J1.6; also elsewhere on the board
/interface/ADC3: J1.3; also elsewhere on the board
/interface/ADC4: J1.5; also elsewhere on the board
/interface/DAC1: J2.1; also elsewhere on the board
/interface/DAC2: J2.2; also elsewhere on the board
/interface/GPIO1: J2.12; also elsewhere on the board
/interface/GPIO2: J2.10; also elsewhere on the board
/interface/GPIO3: J2.8; also elsewhere on the board
/interface/GPIO4: J2.6; also elsewhere on the board
/interface/I2C_SCL: J2.9; also elsewhere on the board
/interface/I2C_SDA: J2.7; also elsewhere on the board
GND: J1.1, J2.11; also elsewhere on the board

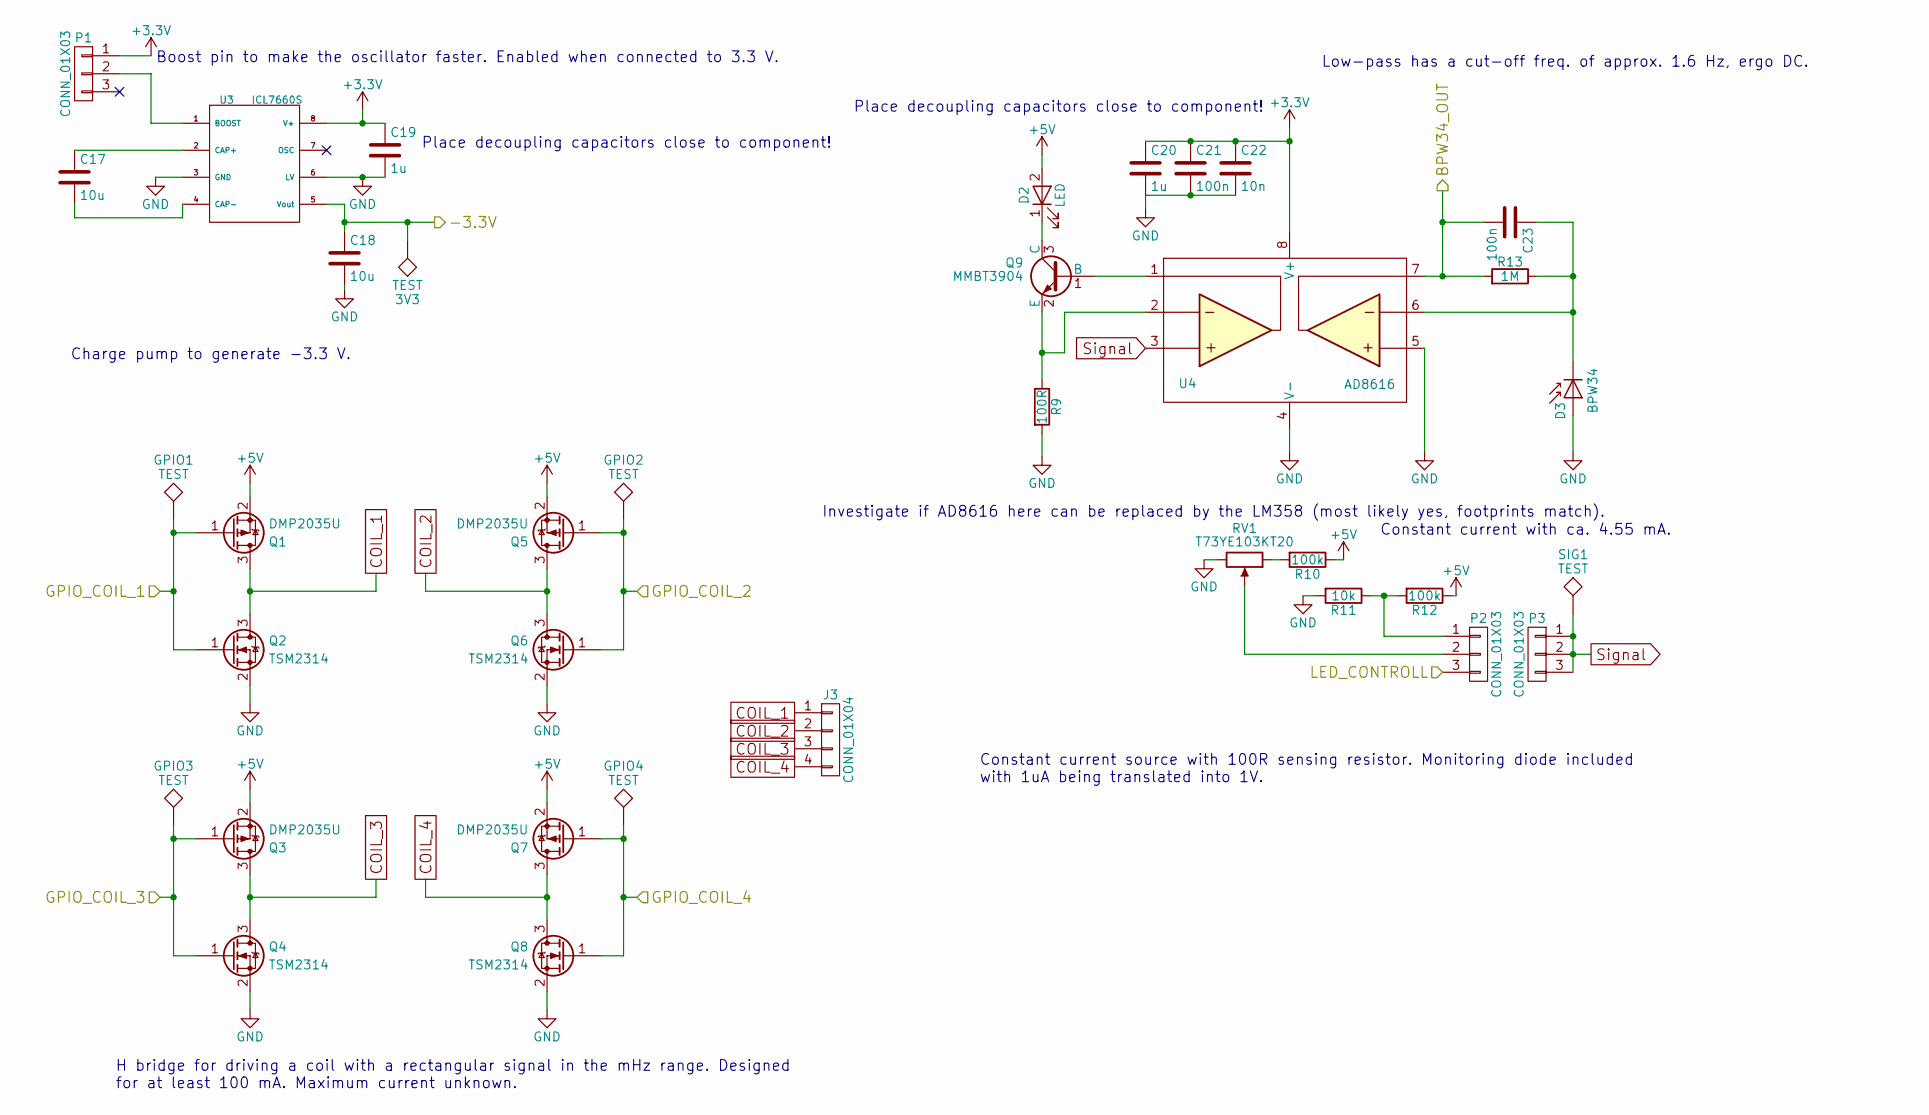
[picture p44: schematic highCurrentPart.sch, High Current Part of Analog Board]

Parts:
3V3: TEST; TP_SMD_quadr_1mm
C17, C18: 10u; R_0805; Farnell 1833812
C19: 1u; R_0805; Farnell 1845751
C20: 1u; R_0805; Farnell 2496946
C21, C23: 100n; R_0805; Farnell 499687
C22: 10n; R_0805; Farnell 1414662
D2: LED; LED_D5.0mm
D3: BPW34; BPW34FA; Farnell 1045425
GPIO1, GPIO2, GPIO3, GPIO4: TEST; TP_SMD_quadr_1mm
J3: CONN_01X04; LED_CONN_1.25_PITCH
P1, P2, P3: CONN_01X03; Samtec-PHT-1-3-01-L-S
Q1, Q3, Q5, Q7: DMP2035U; SOT-23; Farnell 2061419
Q2, Q4, Q6, Q8: TSM2314; SOT-23; Farnell 1864589
Q9: MMBT3904; SOT-23; Farnell 1757935
R9: 100R; R_0805; Farnell 1632456
R10, R12: 100k; R_0805; Farnell 2447551
R11: 10k; R_0805; Farnell 9237755
R13: 1M; R_0805; Farnell 1576507
RV1: T73YE103KT20; Vishay_T73YE103KT20; Farnell 2550676
SIG1: TEST; TP_SMD_quadr_1mm
U3: ICL7660S; SOIC-8-N; Farnell 1561969
U4: AD8616; SOIC-8-N; Farnell 1581952

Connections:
+3V3: C19.1, C20.1, C21.1, C22.1, P1.1, U3.8 (V+), U4.8 (V+); also elsewhere on the board
+5V: D2.2 (A), Q1.2 (S), Q3.2 (S), Q5.2 (S), Q7.2 (S), R10.1, R12.1; also elsewhere on the board
/highCurrentPart/-3.3V: 3V3.1, C18.1, U3.5 (Vout); also elsewhere on the board
/interface/ADC4: C23.2, R13.2, U4.7; also elsewhere on the board
/interface/DAC1: P2.3; also elsewhere on the board
/interface/GPIO1: GPIO1.1, Q1.1 (G), Q2.1 (G); also elsewhere on the board
/interface/GPIO2: GPIO2.1, Q5.1 (G), Q6.1 (G); also elsewhere on the board
/interface/GPIO3: GPIO3.1, Q3.1 (G), Q4.1 (G); also elsewhere on the board
/interface/GPIO4: GPIO4.1, Q7.1 (G), Q8.1 (G); also elsewhere on the board
COIL_1: J3.1, Q1.3 (D), Q2.3 (D)
COIL_2: J3.2, Q5.3 (D), Q6.3 (D)
COIL_3: J3.3, Q3.3 (D), Q4.3 (D)
COIL_4: J3.4, Q7.3 (D), Q8.3 (D)
GND: C18.2, C19.2, C20.2, C21.2, C22.2, D3.2 (A), Q2.2 (S), Q4.2 (S), Q6.2 (S), Q8.2 (S), R9.2, R11.2, RV1.3, U3.3 (GND), U3.6 (LV), U4.4 (V-), U4.5; also elsewhere on the board
unnamed: C17.1, U3.2 (CAP+)
unnamed: C17.2, U3.4 (CAP-)
unnamed: C23.1, D3.1 (K), R13.1, U4.6
unnamed: D2.1 (K), Q9.3 (C)
unnamed: P1.2, U3.1 (BOOST)
unnamed: P2.1, R11.1, R12.2
unnamed: P2.2, RV1.2
unnamed: Q9.1 (B), U4.1
unnamed: Q9.2 (E), R9.1, U4.2
unnamed: R10.2, RV1.1
Signal: P3.1, P3.2, P3.3, SIG1.1, U4.3; also elsewhere on the board

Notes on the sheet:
Place decoupling capacitors close to component!
Constant current source with 100R sensing resistor. Monitoring diode included with 1uA being translated into 1V.
Constant current with ca. 4.55 mA.
H bridge for driving a coil with a rectangular signal in the mHz range. Designed for at least 100 mA. Maximum current unknown.
Boost pin to make the oscillator faster. Enabled when connected to 3.3 V.
Charge pump to generate -3.3 V.
Low-pass has a cut-off freq. of approx. 1.6 Hz, ergo DC.
Investigate if AD8616 here can be replaced by the LM358 (most likely yes, footprints match).

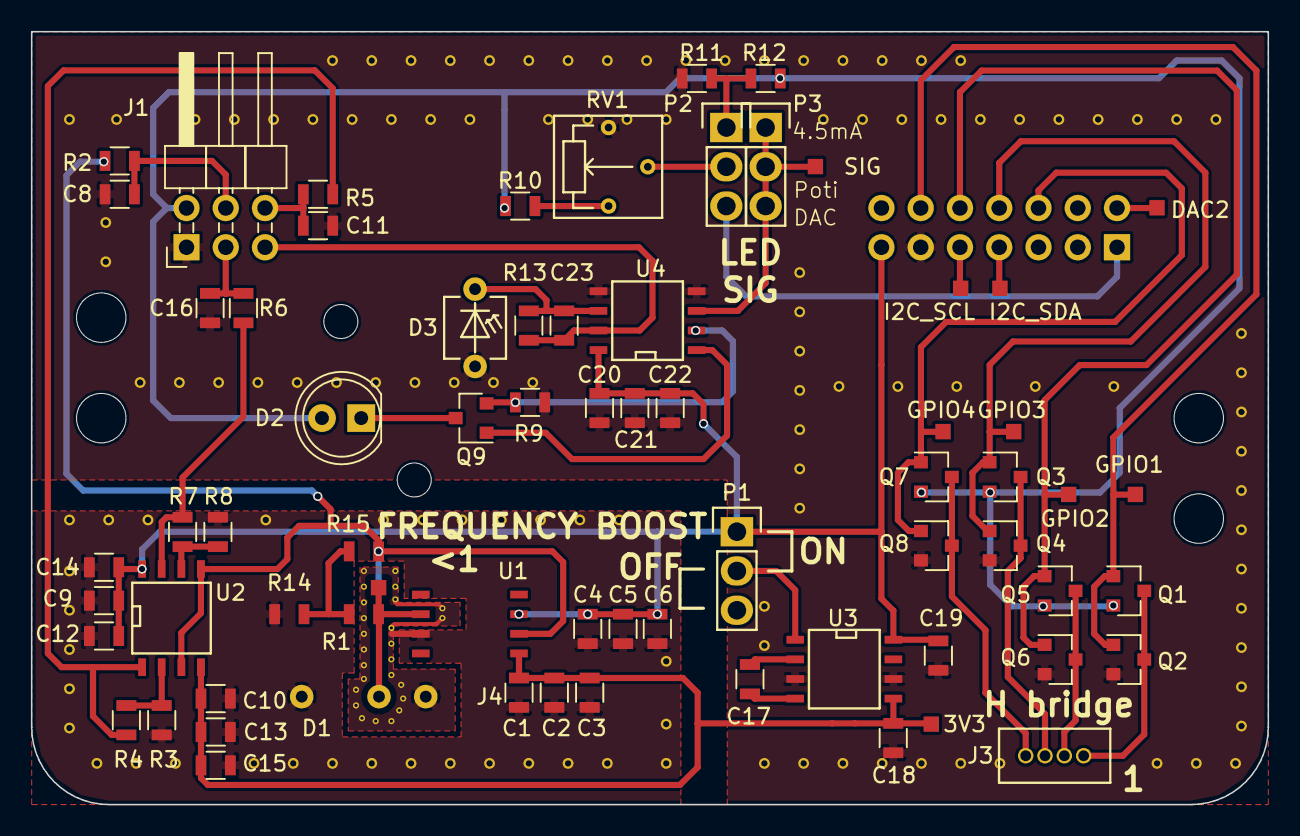
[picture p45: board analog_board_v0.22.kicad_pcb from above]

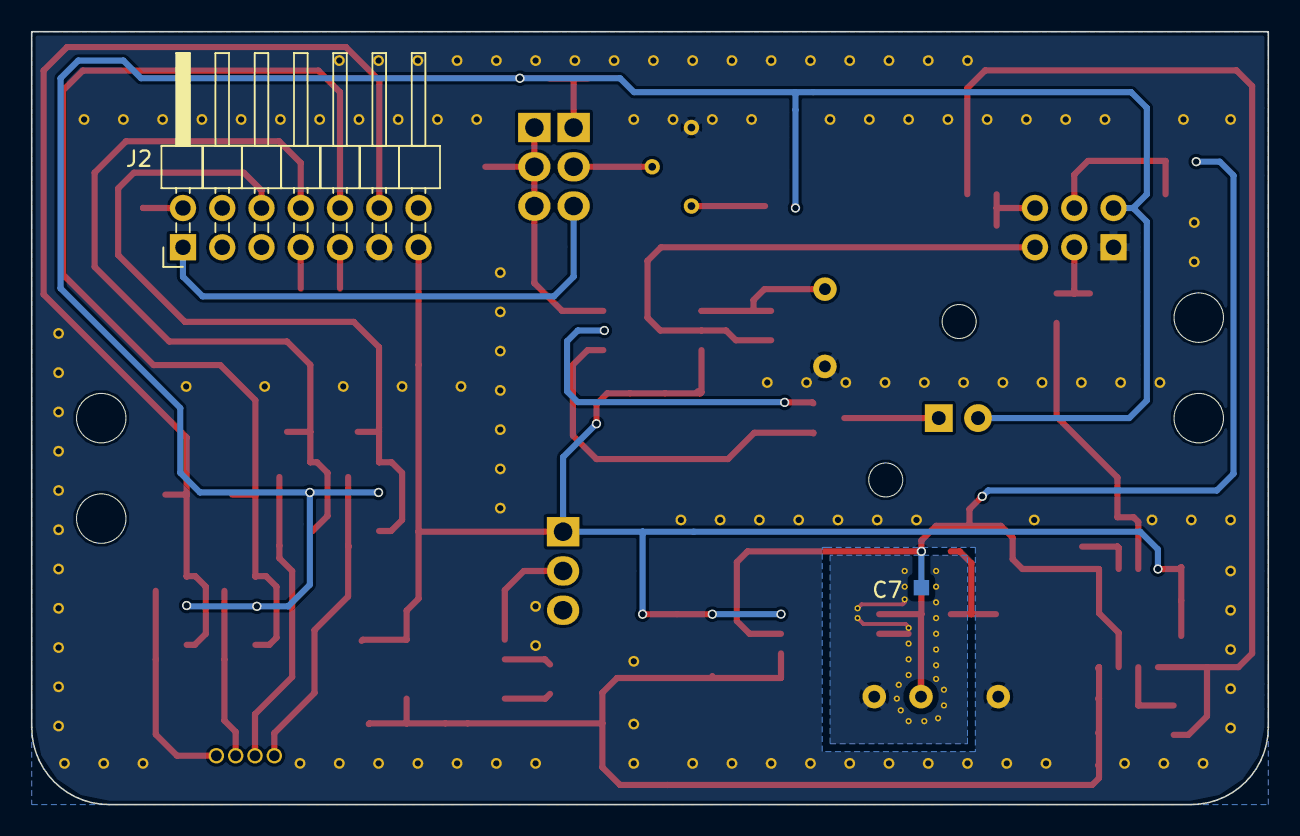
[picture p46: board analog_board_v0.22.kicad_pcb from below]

Board: 2 copper layers, 80.0 x 50.0 mm, 71 parts (2 on the bottom side), 38 nets.

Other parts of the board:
DAC2: DAC2; TP_SMD_quadr_1mm
I2C_SCL, I2C_SDA: TEST; TP_SMD_quadr_1mm
SIG: TEST; TP_SMD_quadr_1mm

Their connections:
/interface/DAC2: DAC2.1; also elsewhere on the board
/interface/I2C_SCL: I2C_SCL.1; also elsewhere on the board
/interface/I2C_SDA: I2C_SDA.1; also elsewhere on the board
Signal: SIG.1; also elsewhere on the board

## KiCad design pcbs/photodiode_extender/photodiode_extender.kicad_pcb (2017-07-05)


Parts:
D1: D_Photo; BPW34FA_w_Silks
J1, J2: CONN_01X01; Pin_Header_Angled_1x01_Pitch2.54mm_W_Silkscreen
J3: CONN_01X01; Pin_Header_Angled_1x01_Pitch2.54mm

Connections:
GNDA: J1.1
unnamed: D1.1 (K), J2.1
unnamed: D1.2 (A), J3.1


Board: 2 copper layers, 15.0 x 20.0 mm, 4 parts (0 on the bottom side), 2 nets.

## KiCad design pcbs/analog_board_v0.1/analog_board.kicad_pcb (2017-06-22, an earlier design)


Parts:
P1: CONN_01X04; LED_CONN_1.25_PITCH
TP1, TP2: TEST; TP_SMD_quadr_3mm

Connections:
+5V: P1.4, TP1.1; also elsewhere on the board
/highCurrent/BPW34_OUT: P1.1; also elsewhere on the board
/lowCurrent/BPW34FA_OUT: P1.2; also elsewhere on the board
GND: P1.3, TP2.1; also elsewhere on the board

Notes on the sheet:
Division of the board in a high power part and a lower power part is crucial to avoid noise in the readout circuit.

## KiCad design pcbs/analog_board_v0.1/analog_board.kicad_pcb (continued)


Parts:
C1: 1u; R_0805; Farnell 2496946
C2: 100n; R_0805; Farnell 499687
C3: 10n; R_0805; Farnell 1414662
C4: 100p; R_0805; Farnell 2332782
C5: 10p; R_0805; Farnell 1759191
C6: 1p; R_0805; Farnell 1759179
D1: LED; LED-5MM
D2: BPW34; BPW34FA; Farnell 1045425
P2, P3, P4, P5: CONN_01X03; Samtec-PHT-1-3-01-L-S
Q1: MMBT3904; SOT-23; Farnell 1757936RL
R1, R3: 100k; R_0805; Farnell 2447551
R2: 10k; R_0805; Farnell 9237755
R4: 100R; R_0805; Farnell 2504961
R5: 1M; R_0805; Farnell 1576507
R6: 10M; R_0805; Farnell 9238115
R7: 100M; R_0805; Farnell 9236511
RV1: T73YE103KT20; Vishay_T73YE103KT20; Farnell 2550676
TP3: TEST; TP_SMD_quadr_3mm
TP4, TP5, TP6: TEST; TP_SMD_quadr_1mm
U1: AD8616; SOIC-8-N; Farnell AD8616ARZ

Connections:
+5V: C1.1, C2.1, C3.1, D1.2 (A), R1.1, R3.1, U1.8 (V+); also elsewhere on the board
/highCurrent/BPW34_OUT: P4.1, P4.2, P4.3, U1.7; also elsewhere on the board
GND: C1.2, C2.2, C3.2, D2.2 (A), P2.3, R2.2, R4.2, RV1.3, U1.4 (V-), U1.5; also elsewhere on the board
unnamed: C4.1, P5.1, R5.1, TP4.1
unnamed: C4.2, C5.2, C6.2, D2.1 (K), R5.2, R6.2, R7.2, U1.6
unnamed: C5.1, P5.2, R6.1, TP5.1
unnamed: C6.1, P5.3, R7.1, TP6.1
unnamed: D1.1 (K), Q1.3 (C)
unnamed: P2.1, R2.1, R3.2
unnamed: P2.2, RV1.2
unnamed: Q1.1 (B), U1.1
unnamed: Q1.2 (E), R4.1, U1.2
unnamed: R1.2, RV1.1
Signal: P3.1, P3.2, P3.3, TP3.1, U1.3

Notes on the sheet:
Place decoupling capacitors close to component!
Constant current source with 100R sensing resistor.
Constant current with ca. 4.55 mA.


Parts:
C7: 1u; R_0805; Farnell 2496946
C8: 100n; R_0805; Farnell 499687
C9: 10n; R_0805; Farnell 1414662
C10: 1p; R_0805; Farnell 1759179
D3: BPW34; BPW34FA; Farnell 1045425
P6, P7: CONN_01X03; Samtec-PHT-1-3-01-L-S
R8: 100k; R_0805; Farnell 2447551
R9: 10k; R_0805; Farnell 9237755
R10: 1K; R_0805; Farnell 9237496
R11: 0.1k; R_0805; Farnell 2504961
R12: 10M; R_0805; Farnell 9238115
U2: AD8616; SOIC-8-N; Farnell AD8616ARZ

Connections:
+5V: C7.1, C8.1, C9.1, U2.8 (V+); also elsewhere on the board
/lowCurrent/BPW34FA_OUT: C10.2, R8.1, U2.3, U2.7; also elsewhere on the board
GND: C7.2, C8.2, C9.2, D3.2 (A), P6.1, P6.2, P6.3, U2.4 (V-), U2.5; also elsewhere on the board
unnamed: C10.1, D3.1 (K), R12.2, U2.6
unnamed: P7.1, R9.1
unnamed: P7.2, R10.1
unnamed: P7.3, R11.1
unnamed: R8.2, R9.2, R10.2, R11.2, R12.1
unnamed: U2.1, U2.2

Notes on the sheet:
Place decoupling capacitors close to component!


Board: 2 copper layers, 80.0 x 50.0 mm, 42 parts (1 on the bottom side), 21 nets.

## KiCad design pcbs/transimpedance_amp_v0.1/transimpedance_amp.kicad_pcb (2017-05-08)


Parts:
C1, C10: 1p; R_0805
C2, C9: 10p; R_0805
C3, C8: 100p; R_0805
C4, C7: 1n; R_0805
C5, C6: 10n; R_0805
D1: BPW34FA
D2: BPW34; BPW34FA; Farnell 1045425
P1, P2, P3, P4, P5, P6, P7, P8: CONN_01X05; Pin_Header_Straight_1x05
R1, R10: 100M; R_0805
R2, R9: 10M; R_0805
R3, R8: 1M; R_0805
R4, R7: 100k; R_0805
R5, R6: 10k; R_0805
TP1, TP2, TP3, TP4: TEST; TP_SMD_quadr_3mm
U1: AD8616; SOIC-8-N; Farnell AD8616ARZ

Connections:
+5V: TP2.1, U1.8 (V+); also elsewhere on the board
GND: D1.2 (A), D2.2 (A), TP3.1, U1.2, U1.4 (V-), U1.6; also elsewhere on the board
unnamed: C1.1, P2.5, P3.5, R1.1
unnamed: C1.2, C2.2, C3.2, C4.2, C5.2, D1.1 (K), R1.2, R2.2, R3.2, R4.2, R5.2, U1.3
unnamed: C2.1, P2.4, P3.4, R2.1
unnamed: C3.1, P2.3, P3.3, R3.1
unnamed: C4.1, P2.2, P3.2, R4.1
unnamed: C5.1, P2.1, P3.1, R5.1
unnamed: C6.1, P6.1, P8.1, R6.1
unnamed: C7.1, P6.2, P8.2, R7.1
unnamed: C8.1, P6.3, P8.3, R8.1
unnamed: C9.1, P6.4, P8.4, R9.1
unnamed: C10.1, P6.5, P8.5, R10.1
unnamed: C6.2, C7.2, C8.2, C9.2, C10.2, D2.1 (K), R6.2, R7.2, R8.2, R9.2, R10.2, U1.5
unnamed: P1.1, P1.2, P1.3, P1.4, P1.5, U1.1
unnamed: P4.1, P4.2, P4.3, P4.4, P4.5, TP1.1
unnamed: P5.1, P5.2, P5.3, P5.4, P5.5, TP4.1
unnamed: P7.1, P7.2, P7.3, P7.4, P7.5, U1.7


Board: 2 copper layers, 80.0 x 50.0 mm, 35 parts (0 on the bottom side), 18 nets.

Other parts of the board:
5V: TEST; TP_SMD_quadr_3mm
GND: TEST; TP_SMD_quadr_3mm

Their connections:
+5V: 5V.1; also elsewhere on the board
GND: GND.1; also elsewhere on the board

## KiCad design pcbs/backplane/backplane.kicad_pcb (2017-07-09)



Board: 2 copper layers, 80.0 x 50.0 mm, 59 parts (32 on the bottom side), 44 nets.

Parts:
3V3, 5V: TEST; TP_SMD_quadr_1mm
ADC1, ADC2, ADC3, ADC4: TEST; TP_SMD_quadr_1mm
C1, C10, C11: 10u; R_0805
C2, C4, C8: 1u; R_0805
C3, C5, C9, C12, C13: 100n; R_0805
C6, C7: 22p; R_0805
D1, D2, D3, D4, D5, D6: LED; LED_0805
DAC1, DAC2: TEST; TP_SMD_quadr_1mm
GND, GND1: TEST; TP_SMD_quadr_3mm
J1: CONN_01X04; LED_CONN_1.25_PITCH
J2: CONN_01X01; Samtec-PHT-1-1-01-L-S
P1: USB_B; ZX62D-B-5P8(30)
P2, P7, P8: CONN_01X03; Samtec-PHT-1-3-01-L-S
P3, P4: CONN_02X03; Pin_Header_Straight_2x03
P5, P6: CONN_02X07; Pin_Header_Straight_2x07
Q1, Q2: MMBT3904; SOT-23
Q3: Si2323; SOT-23
R1, R2, R3, R4, R7, R8: 1k; R_0805
R5, R6: 10k; R_0805
R9, R10: 470R; R_0805
SCL: TEST; TP_SMD_quadr_1mm
SDA: TEST; TP_SMD_quadr_1mm
U1, U3: LM358; SOIC-8-N
U2: TC1262-33VDB; SOT-223
U4: CH340G; SO-16-N
Y1: Crystal; Crystal_SMD_HC49-SD

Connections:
3.3V: 3V3.1, C4.1, C5.1, C8.1, C9.1, P5.1, P6.1, P7.1, U2.3, U4.4, U4.16
5V: 5V.1, C1.1, C2.1, C3.1, P2.1, P3.1, P4.1, Q3.2, U2.1
5V_BATT: J1.1, J1.2, P8.3
5V_USB: P1.1, P8.1
ADC1: ADC1.1, P3.3, P4.3
ADC2: ADC2.1, P3.5, P4.5
ADC3: ADC3.1, P3.4, P4.4
ADC4: ADC4.1, P3.6, P4.6
D+: P1.3, U4.5
D-: P1.2, U4.6
DAC1: DAC1.1, P5.13, P6.13
DAC2: DAC2.1, P5.14, P6.14
DTR: Q2.2, R5.2, U4.13
GND: C1.2, C2.2, C3.2, C4.2, C5.2, C6.2, C7.2, C8.2, C9.2, C10.2, C11.2, C12.2, C13.2, D5.1, D6.1, GND.1, GND1.1, J1.3, J1.4, J2.1, P1.5, P3.2, P4.2, P5.3, P6.3, Q3.1, U1.4, U2.2, U2.4, U3.4, U4.1
GPIO0: P5.2, Q2.3
GPIO1: P5.4, P6.4
GPIO2: P5.6, P6.6
GPIO3: P5.8, P6.8
GPIO4: P5.10, P6.10
I2C_SCL: P5.5, P6.5, SCL.1, U3.3
I2C_SDA: P5.7, P6.7, SDA.1, U3.5
LED_3.3V: P7.2, R8.2
LED_5V: C10.1, C11.1, C12.1, C13.1, D1.2, D2.2, D3.2, D4.2, P2.2, R7.2, U1.8, U3.8
unnamed: C6.1, U4.7, Y1.2
unnamed: C7.1, U4.8, Y1.1
unnamed: D1.1, R1.1
unnamed: D2.1, R2.1
unnamed: D3.1, R3.1
unnamed: D4.1, R4.1
unnamed: D5.2, R7.1
unnamed: D6.2, R8.1
unnamed: P8.2, Q3.3
unnamed: Q1.1, R5.1
unnamed: Q2.1, R6.1
unnamed: R1.2, U1.1, U1.2
unnamed: R2.2, U1.6, U1.7
unnamed: R3.2, U3.1, U3.2
unnamed: R4.2, U3.6, U3.7
unnamed: R9.1, U4.2
unnamed: R10.1, U4.3
RTS: Q1.2, R6.2, U4.14
UART_RX: P5.11, R10.2, U1.3
UART_TX: P5.9, R9.2, U1.5
nRST: P5.12, Q1.3

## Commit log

2017-04-10 Added papers.
    [first_experiment.csv]
2017-04-10 Added a opamp model.
    [first_experiment.csv]
2017-04-11 Added aditional trans. amp. simulations for other currents.
    [first_experiment.csv]
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2017-04-13 More stuff.
    [current.csv, first_experiment.csv, transimp.csv]
2017-04-13 Updated shopping list.
    [transimp.csv]
2017-04-13 completion of the current bom
    [current.csv]
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2017-04-13 completed bom
    [current.csv]
2017-04-13 start with pcb
    [CurrentSource.PrjPcb, currentsource.SchDoc]
2017-04-13 Current source pcb
    [CurrentSource.PrjPcb, currentsource.PcbDoc, currentsource.SchDoc]
2017-04-18 Adding a CAD file.
    [playing.scad]
2017-04-24 Started layouting prototype v0.1.
    [transimpedance_amp.kicad_pcb, transimpedance_amp.sch]
2017-04-25 Done with layouting so far.
    [transimpedance_amp.kicad_pcb, transimpedance_amp.sch]
2017-04-25 Finished layout of transimpedance amplifier.
    [transimpedance_amp.kicad_pcb]
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2017-04-25 Almost finished first version pcb
    [CurrentSource.PrjPcb, currentsource.PcbDoc]
2017-04-25 added right angle
    [current.csv]
2017-04-25 Finished the first pcb
    [currentsource.PcbDoc, currentsource.SchDoc]
2017-04-25 Removed components in inventory
    [current.csv]
2017-04-26 Started with housing. It is already nice.
    [open_box.scad, playing.scad, transimpedance_amp.kicad_pcb]
2017-04-26 Quite far with the housing.
    [open_box.scad, playing.scad]
2017-04-27 Fixed a couple of bugs in the open box module. Now it is bravo.
    [housing.scad, open_box.scad]
2017-04-27 Almost done with the design.
    [housing.scad, open_box.scad]
2017-04-28 Housing ready for first experiments.
    [housing.scad]
2017-04-28 Forgot to add some stuff.
    [adapter.scad, adapter.stl, housing.stl, lid.scad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]
2017-04-28 Found a design error. Has to be corrected.
    [transimpedance_amp.kicad_pcb, transimpedance_amp.sch]
2017-05-01 Finished layout. Sill room for optimization.
    [transimpedance_amp.kicad_pcb, transimpedance_amp.sch]
2017-05-01 Finished transimpedance amp. layout. Produced output for v0.1.
    [transimpedance_amp.kicad_pcb]
2017-05-03 Started project for etching.
    [part_list.csv]
2017-05-03 Changed list.
    [part_list.csv]
2017-05-03 Added budget.
    [budget.csv]
2017-05-03 Rev.1 + Gerbers
    [CurrentSource.PrjPcb, currentsource.PcbDoc, currentsource.gbl, currentsource.gbo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]
2017-05-03 Created gerber files.
    [part_list.csv, transimpedance_amp-B.CrtYd.gbr, transimpedance_amp-B.Cu.gbr, transimpedance_amp-B.Mask.gbr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]
2017-05-08 Orders for etching added.
    [part_list.csv, transimpedance_amp.kicad_pcb, transimpedance_amp.sch]
2017-05-13 Produced some nice pcitures for brochure.
    [housing.scad]
2017-05-18 Changed allowances to mostly 0.2 mm. Made walls thicker.
    [adapter.scad, adapter.stl, housing.scad, housing.stl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]
2017-05-23 Optimized some stuff. Hope to be bug free now.
    [adapter.scad, adapter.step, adapter.stl, housing.scad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]
2017-06-07 Finished drill press adapter.
    [adapter_drilling_machine.scad, adapter_drilling_machine.stl, open_box.scad]
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2017-06-09 Finished a PCB holder for etching.
    [pcb_holder_crossbar.scad, pcb_holder_frame.scad, pcb_holder_holder_l.scad, pcb_holder_holder_r.scad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]
2017-06-09 Cleaned up.
    [tets.fcstd, tets2.fcstd]
2017-06-10 Improved the PCB holder.
    [pcb_holder_crossbar.scad, pcb_holder_crossbar.stl, pcb_holder_holder_l.scad, pcb_holder_holder_l.stl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]
2017-06-12 Finished etching machine design.
    [adapter_drilling_machine.scad, adapter_drilling_machine.stl, pcb_holder_crossbar.scad, pcb_holder_crossbar.stl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]
2017-06-12 Added a floor protection for cuvette. One doublecheck left.
    [pcb_holder_crossbar.scad, pcb_holder_crossbar.stl, pcb_holder_floor_prot.scad, pcb_holder_floor_prot.stl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]
2017-06-13 Simulation done for today.
    [transimpedance_amp-B.CrtYd.gbr, transimpedance_amp-B.Cu.gbr, transimpedance_amp-B.Mask.gbr, transimpedance_amp-B.SilkS.gbr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]
2017-06-13 Started layouting new board.
    [analog_board.kicad_pcb, analog_board.sch, highCurrent.sch, lowCurrent.sch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]
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2017-06-14 Added some mounting holes.
    [analog_board.kicad_pcb, analog_board.sch, highCurrent.sch, lowCurrent.sch]
2017-06-17 Almost done with the etching machine CAD work.
    [analog_board.kicad_pcb, dimensions.scad, highCurrent.sch, lowCurrent.sch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]
2017-06-20 Started working on a backplane.
    [backplane.kicad_pcb, backplane.sch, dimensions.scad, pcb_holder_crossbar.scad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]
2017-06-22 Small adoptions for the glass silde to be put on the analog PCB directly.
    [adapter.scad, adapter.step, adapter.stl, adapter_drilling_machine.scad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]
2017-06-22 Made the LED illuminator a little bit smaller.
    [led_illuminator.scad]
2017-06-25 Updated electrical spec.
    [backplane.sch]
2017-06-25 Mechanical specs updated.
    [backplane.kicad_pcb]
2017-06-25 Changed electrical spec again.
    [_saved_highCurrent.sch, backplane.sch]
2017-06-26 Schematics of backplane done.
    [_saved_highCurrent.sch, backplane.sch]
2017-06-26 Came quite far with backplane design. Not finished yet.
    [backplane.kicad_pcb, backplane.sch]
2017-06-27 Backplane version 1 ready.
    [backplane.kicad_pcb, backplane.sch]
2017-06-28 Simulated a lot today. Ideas for the new transimpedance amp. are there.
    [backplane.FCStd, backplane.kicad_pcb, backplane.step]
2017-06-29 Simulated the new transimpedance amp.
    [analog_board.kicad_pcb, analog_board.sch, backplane.FCStd, backplane.kicad_pcb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]
2017-06-30 Finished schematics of the analog_board_v0.2 today.
    [analog_board.kicad_pcb, analog_board.sch, analog_board_v0.2.kicad_pcb, analog_board_v0.2.sch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]
2017-07-02 Added some iportant backplane spec.
    [analog_board_v0.2.sch, backplane.kicad_pcb, highCurrentPart.sch, interface.sch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]
2017-07-02 Resolved issue where the pins to the backboard were flipped
    [uppsense.PcbDoc, uppsense.SchDoc]
2017-07-03 Analog board basically finished.
    [analog_board_v0.2.kicad_pcb, analog_board_v0.2.sch, highCurrentPart.sch, sensitiveReadout.sch]
2017-07-04 Small changes on the backplane standing out.
    [analog_board_v0.2.kicad_pcb, analog_board_v0.2.sch, backplane.FCStd, backplane.kicad_pcb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]
2017-07-04 Backplane definitely finished. Somethings wrong with TIA. Has to be checked tomorrow.
    [analog_board_v0.2.kicad_pcb, backplane.kicad_pcb, backplane.sch, highCurrentPart.sch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]
2017-07-05 Finished the photo extender, backplane and the analog board.
    [analog_board_v0.2.kicad_pcb, analog_board_v0.2.sch, backplane.kicad_pcb, backplane.sch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]
2017-07-05 Added BOMs and gerber files.
    [analog_board_v0.2-B.Cu.gbr, analog_board_v0.2-B.Mask.gbr, analog_board_v0.2-B.SilkS.gbr, analog_board_v0.2-Edge.Cuts.gbr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]
2017-07-06 Four boards in less than two weeks :D
    [analog_board_v0.22-B.Cu.gbr, analog_board_v0.22-B.Mask.gbr, analog_board_v0.22-B.SilkS.gbr, analog_board_v0.22-Edge.Cuts.gbr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]
2017-07-08 Release Candidate 1. moved headers, added RC filters
    [uppsense.PcbDoc, uppsense.SchDoc]
2017-07-08 Reverted header
    [uppsense.PcbDoc, uppsense.SchDoc]
2017-07-09 added temp sensor Added Gerbers
    [uppsense.PcbDoc, uppsense.PrjPcb, uppsense.SchDoc, uppsense.gbl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]
2017-07-09 Mechanics developed further.
    [analog_board_v0.2-B.Cu.gbr, analog_board_v0.2-B.Mask.gbr, analog_board_v0.2-B.SilkS.gbr, analog_board_v0.2-Edge.Cuts.gbr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]
2017-07-10 Updated BOM.
    [analog_board_v0.22.csv, bom.csv, photodiode_extender-B.Cu.gbr, photodiode_extender-B.Mask.gbr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]
2017-07-10 Updated bom with some of the logic components
    [bom.csv]
2017-07-10 Finalized BOM, ESP and DAC are missing on farnel
    [bom.csv]
2017-07-11 Worked on emchnaics.
    [dimensions.scad, main.scad]
2017-07-11 Modified BOM.
    [bom.csv]
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2017-07-22 Removed tenting from the ic's. Sorry! shifted one connector
    [uppsense.PcbDoc, uppsense.PrjPcb, uppsense.SchDoc]
2017-07-28 Box seems to be finished.
    [analog_board_v0.22.sch, backplane.sch, box.scad, dimensions.scad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]
2017-07-28 Housing finished. Final checks outstanding.
    [box.scad, dimensions.scad, lid_f_b.scad, lid_l_r.scad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]
2017-07-29 Housing finished. STLs produced.
    [box.scad, box.stl, dimensions.scad, glass_slide_holder.scad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]
2017-07-29 Finished glass slide holder.
    [dimensions.scad, glass_holder.scad, legs.scad, main.scad]
2017-07-29 Forgot sth.
    [glass_slide_holder.stl]
2017-07-31 Made meachnical design better for FDM.
    [analog_board_v0.2.kicad_pcb, box.scad, box_female.scad, box_female.stl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]
2017-08-01 Final checks and rotating.
    [box_female.stl, box_male.stl, dimensions.scad, lid_back.stl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]
2017-08-02 Updated the glass slide holder.
    [analog_board_v0.2.kicad_pcb, analog_board_v0.22.kicad_pcb, dimensions.scad, glass_holder.scad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]
2017-08-07 Started working on mechanics rev 5.
    [box.scad, box_female.scad, box_female.stl, box_male.scad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]
2017-08-07 Modified the mechanics a bit to be able to print everything once more.
    [box_female.scad, box_female.stl, box_male.scad, box_male.stl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]
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
